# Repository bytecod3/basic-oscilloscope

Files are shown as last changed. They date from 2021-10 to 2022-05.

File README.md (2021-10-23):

# basic-oscilloscope
Basic Digital Storage Oscilloscope

## Introduction
This oscilloscope uses an STM32F103C8T6 blue pill board as the main MPU for processing and display of output

## Specifications
| Spec | Value |
| ----- | -------|
|Analog bandwidth| 0 - 500kHz|
|Number of channels| 2|
|Sample Rate| 2M Samples/s (configurable)|
|RAM| 2GB (External)|
|Processor| STM32F103C8T6|
|CPU-speed| 72MHz|
|Power input| 9V battery of 12V DC jack input|
|Current| 150mA|
|Screen size| 1.8”|
|Maximum input voltage| 50V pk-pk|
|Time base range| 10uS/Div - 500s/Div|
|Storage| USB-2.0 External flash drive|
|Coupling| AC, DC, GND|
|Input impedance| 1MOhm|
|Record length| 1024|

### Top View
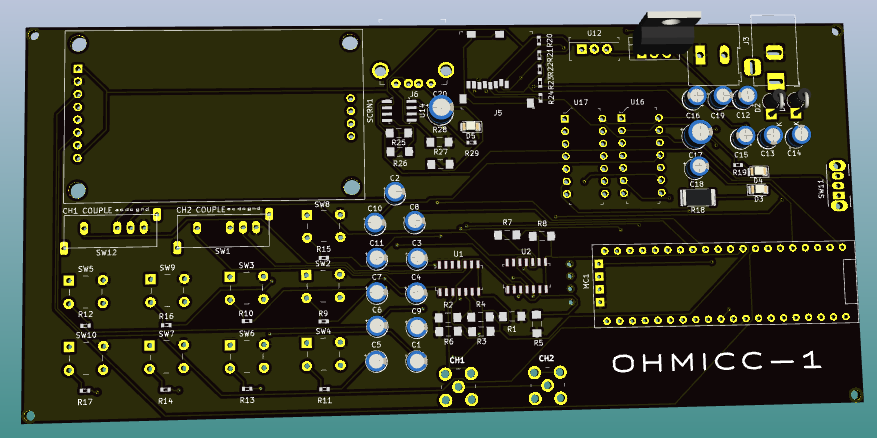
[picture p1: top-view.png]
Top View


### Bottom View
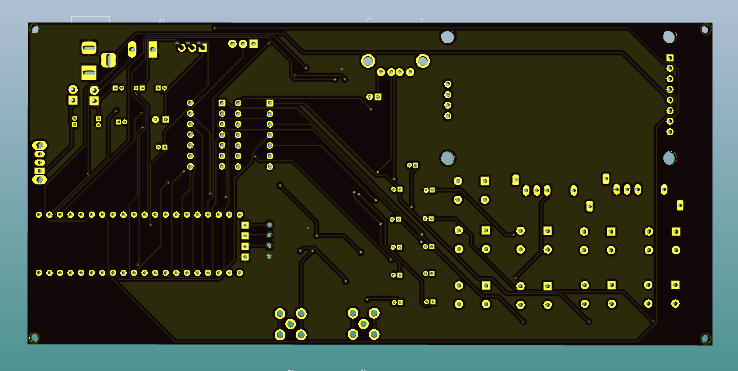
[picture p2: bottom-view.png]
Bottom View


### Left View
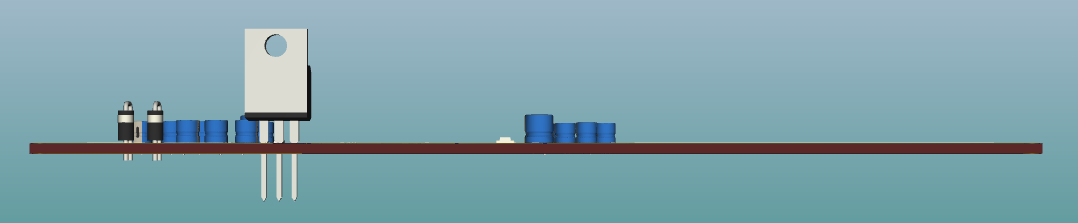
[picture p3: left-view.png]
Left View


### Right View
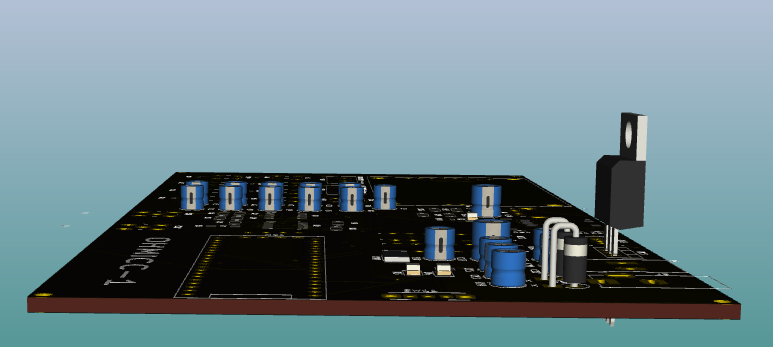
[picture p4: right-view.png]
Right View


## Usage
### Powering 
The oscilloscope uses either 12V DC jack adapter or a 9V battery. You can only use one at a time. 
To use the 12V adapter, plug in the jack into the DC Jack located at the top right of the board. To use the 9V battery,
you should have a battery holder with two wires protruding, for +ve and -ve side. Fix these wires on the terminal block located at the top right corner of the board. 
Finally is to toggle the slide-switch located on the right edge of the board.  
On both cases, a green LED should light indicating that the oscilloscope is fully powered. 

To switch off the oscilloscope, toggle the slide-switch agin to the direction labelled OFF on the board silkscreen.

**CAUTION**: Do not use both 12V adapter and 9V at the same time

## Callibration

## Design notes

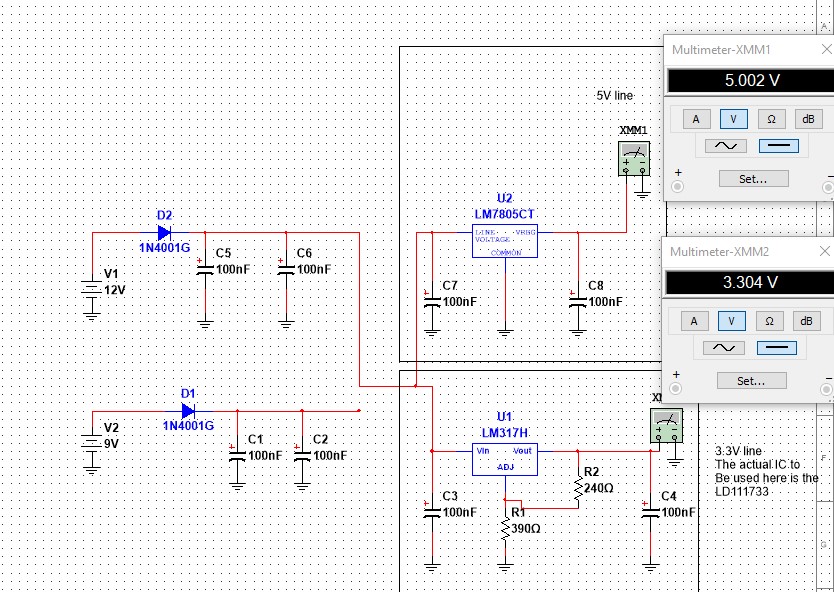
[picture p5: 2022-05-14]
simulations/power-supply/power-supply-simulation.jpg

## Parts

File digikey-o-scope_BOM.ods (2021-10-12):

Reference | Quantity | Value | Footprint | Digi-Key_PN | MPN | Price | Total Price | Part Page
C12 C13 C14 C15 C16 C18 | 6 | 100n | Capacitor_THT:CP_Radial_D4.0mm_P1.50mm | 493-12784-1-ND | UVR1H0R1MDD6TP | $0.30 | $1.80 | https://www.digikey.com/en/products/detail/nichicon/UVR1H0R1MDD6TP/4328371?s=N4IgTCBcDaICwE4DMBaAjGA7ADjulAcgCIgC6AvkA
C17 | 1 | 0.22u | Capacitor_THT:CP_Radial_D5.0mm_P2.50mm | 493-11478-1-ND | URS1HR22MDD1TD | $0.37 | $0.37 | https://www.digikey.com/en/products/detail/nichicon/URS1HR22MDD1TD/4320225?s=N4IgTCBcDaIKoCUDKBGAEgsYCyARXKAKriALoC%2BQA
C20 | 1 | 22u | Capacitor_THT:CP_Radial_D5.0mm_P2.00mm | 1572-1384-ND | 226CKR050M | $0.19 | $0.19 | https://www.digikey.com/en/products/detail/illinois-capacitor/226CKR050M/5411619?s=N4IgTCBcDa5gbAYQNICUAMBWdBZEBdAXyA
C1 C2 C3 C4 C5 C6 C7 C8 C9 C10 C11 C19 | 12 | 0.1u | Capacitor_THT:CP_Radial_D4.0mm_P1.50mm | 493-12784-1-ND | UVR1H0R1MDD6TP | $0.30 | $3.60 | https://www.digikey.com/en/products/detail/nichicon/UVR1H0R1MDD6TP/4328371?s=N4IgTCBcDaICwE4DMBaAjGA7ADjulAcgCIgC6AvkA
D1 D2 | 2 | D | Diode_THT:D_DO-41_SOD81_P2.54mm_Vertical_KathodeUp | 1N4148-P-GICT-ND | 1N4148-P-TR | $0.17 | $0.34 | https://www.digikey.com/en/products/detail/vishay-general-semiconductor-diodes-division/1N4148-P-TR/4826413
D3 D4 D5 | 3 | LED | LED_SMD:LED_1206_3216Metric | 2460-L152L-LWCTR-ND | L152L-LWC | $0.37 | $1.11 | https://www.digikey.com/en/products/detail/american-opto-plus-led/L152L-LWC/12325421
J1 J2 | 2 | 5-1814400-1 | digikey-footprints:RF_SMA_RightAngle_5-1814400-1 | 2057-RF1-07-T-00-75-ND | RF1-07-T-00-75 | $2.49 | $4.98 | https://www.digikey.com/en/products/detail/adam-tech/RF1-07-T-00-75/9832650
J3 | 1 | Jack-DC | Connector_BarrelJack:BarrelJack_Horizontal | 2073-DCJ200-10-A-K1-K-ND | DCJ200-10-A-K1-K | $0.74 | $0.74 | https://www.digikey.com/en/products/detail/gct/DCJ200-10-A-K1-K/9859579
J4 | 1 | Screw_Terminal_01x02 | TerminalBlock:TerminalBlock_Altech_AK300-2_P5.00mm | 1801135-ND | 1801135 | $1.09 | $1.09 | https://www.digikey.com/en/products/detail/phoenix-contact/1801135/4387899?s=N4IgTCBcDaIIwA4AMc4GYCsBaAcgERAF0BfIA
J5 | 1 | Micro_SD_Card | digikey-footprints:MicroSD_2908-05WB-MG | 3M5607CT-ND | 2908-05WB-MG | $3.48 | $3.48 | https://www.digikey.com/en/products/detail/3m/2908-05WB-MG/1242497?s=N4IgTCBcDa4JwAYAcBaBBWA6gIRQWQHEQBdAXyA
J6 | 1 | USB_A | digikey-footprints:USB_A_Female_UE27AC54100 | UE27AC54100-ND | UE27AC54100 | $0.70 | $0.70 | https://www.digikey.com/en/products/detail/amphenol-icc-commercial-products/UE27AC54100/1972253?s=N4IgTCBcDaIKoFEwHYCCBhArAFgIwAZ8QBdAXyA
MC1 | 1 | BLUE-PILL | my-screen:BLUE-PILL | * | * |  | $0.00 | *
R9 R10 R11 R12 R13 R14 R15 R16 R17 R29 | 10 | 1k | digikey-footprints:0603 | 13-RE0603FRE071KLTR-ND | RE0603FRE071KL | $0.10 | $1.00 | https://www.digikey.com/en/products/detail/yageo/RE0603FRE071KL/5923313
R18 | 1 | 100R | Resistor_SMD:R_2512_6332Metric | RMCF2512JT100RTR-ND | RMCF2512JT100R | $0.30 | $0.30 | https://www.digikey.com/en/products/detail/stackpole-electronics-inc/RMCF2512JT100R/1756924?s=N4IgTCBcDaIEoFkDCAxMBWAjGAUgFUwAZC4QBdAXyA
R19 | 1 | 160R | digikey-footprints:0603 | 749-1765-2-ND | MCT06030C1600FP500 | $0.13 | $0.13 | https://www.digikey.com/en/products/detail/vishay-beyschlag-draloric-bc-components/MCT06030C1600FP500/7347856?s=N4IgTCBcDaIOwBYCcBaAjHAbAVhWFAcgCIgC6AvkA
R20 R21 R22 R23 R24 | 5 | 22k | digikey-footprints:0603 | RNCF0603DTE22K0TR-ND | RNCF0603DTE22K0 | $0.13 | $0.65 | https://www.digikey.com/en/products/detail/stackpole-electronics-inc/RNCF0603DTE22K0/6264113
R1 R2 R3 R4 R5 R6 R7 R8 R25 R26 R27 R28 | 12 | 10k | digikey-footprints:1206 | 13-RE1206FRE0710KLTR-ND | RE1206FRE0710KL | $0.10 | $1.20 | https://www.digikey.com/en/products/detail/yageo/RE1206FRE0710KL/5924263?s=N4IgTCBcDaIEoFECMYAMA2AYo1B2JqA0gDIgC6AvkA
SCRN1 | 1 | 1.8"LCD_TFT | my-screen:1.8TFT_SCREEN | * | * |  | $0.00 | *
SW11 | 1 | SW_SPDT | Button_Switch_THT: SW_CuK_OS102011MA1QN1_SPDT_Angled | 2368-54-720-ND | 54-720 | $1.31 | $1.31 | https://www.digikey.com/en/products/detail/nte-electronics-inc/54-720/11647518
SW1 SW12 | 2 | SW_SP3T | my-screen:SP3T_OS103012MU1QP1_SWITCH | CKN9552-ND | OS103012MU1QP1 | $0.85 | $1.70 | https://www.digikey.com/en/products/detail/c-k/OS103012MU1QP1/1981423?s=N4IgTCBcDaIPIGUCMAGAzCpYCyBVJAigApIgC6AvkA
SW2 SW3 SW4 SW5 SW6 SW7 SW8 SW9 SW10 | 9 | SW_MEC_5E | digikey-footprints:Switch_Tactile_THT_6x6mm_MJTP1230 | 679-2428-ND | MJTP1230 | $0.10 | $0.90 | https://www.digikey.com/en/products/detail/apem-inc/MJTP1230/1798037
U12 | 1 | LD1117V33 | digikey-footprints:TO-220-3 | 497-1491-5-ND | LD1117V33 | $0.70 | $0.70 | https://www.digikey.com/en/products/detail/stmicroelectronics/LD1117V33/586012
U13 | 1 | LM7805_TO220 | Package_TO_SOT_THT:TO-220-3_Vertical | 2156-LM7805CT-ND | LM7805CT | $1.11 | $1.11 | https://www.digikey.com/en/products/detail/fairchild-semiconductor/LM7805CT/12600247
U14 | 1 | LM3526-L | digikey-footprints:SOIC-8_W3.9mm | LM3526MX-L/NOPBCT-ND | LM3526MX-L/NOPB | $1.26 | $1.26 | https://www.digikey.com/en/products/detail/texas-instruments/LM3526MX-L-NOPB/367056
U16 U17 | 2 | SN74HC14N | digikey-footprints:DIP-14_W3mm | 296-1577-5-ND | SN74HC14N | $0.23 | $0.46 | https://www.digikey.com/en/products/detail/texas-instruments/SN74HC14N/13504773
U1 U2 | 2 | LM324ADR | digikey-footprints:SOIC-14_W3.9mm | 296-9540-1-ND | LM324ADR | $0.49 | $0.98 | https://www.digikey.com/en/products/detail/texas-instruments/LM324ADR/381227?s=N4IgTCBcDa4JwDYC0cCsAWADEgjEgcgCIgC6AvkA

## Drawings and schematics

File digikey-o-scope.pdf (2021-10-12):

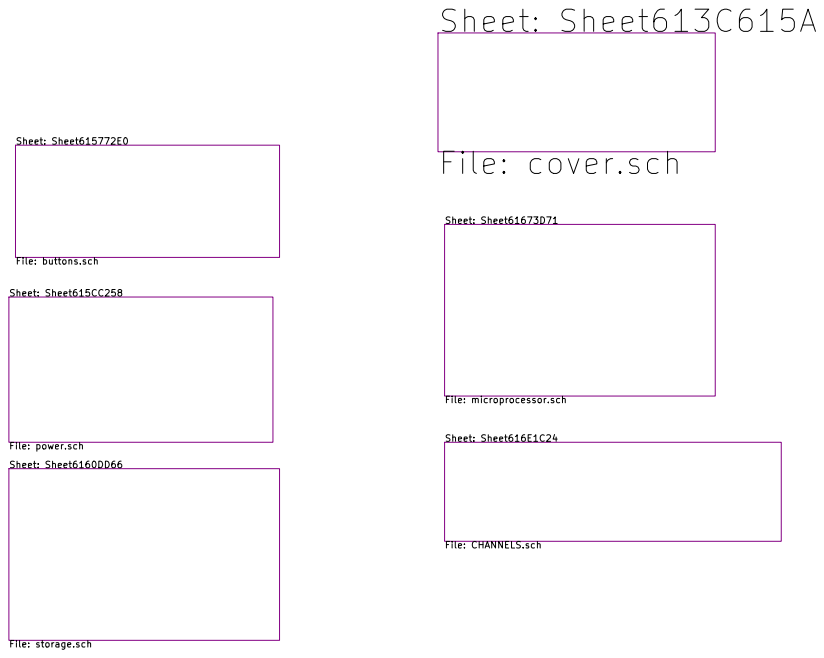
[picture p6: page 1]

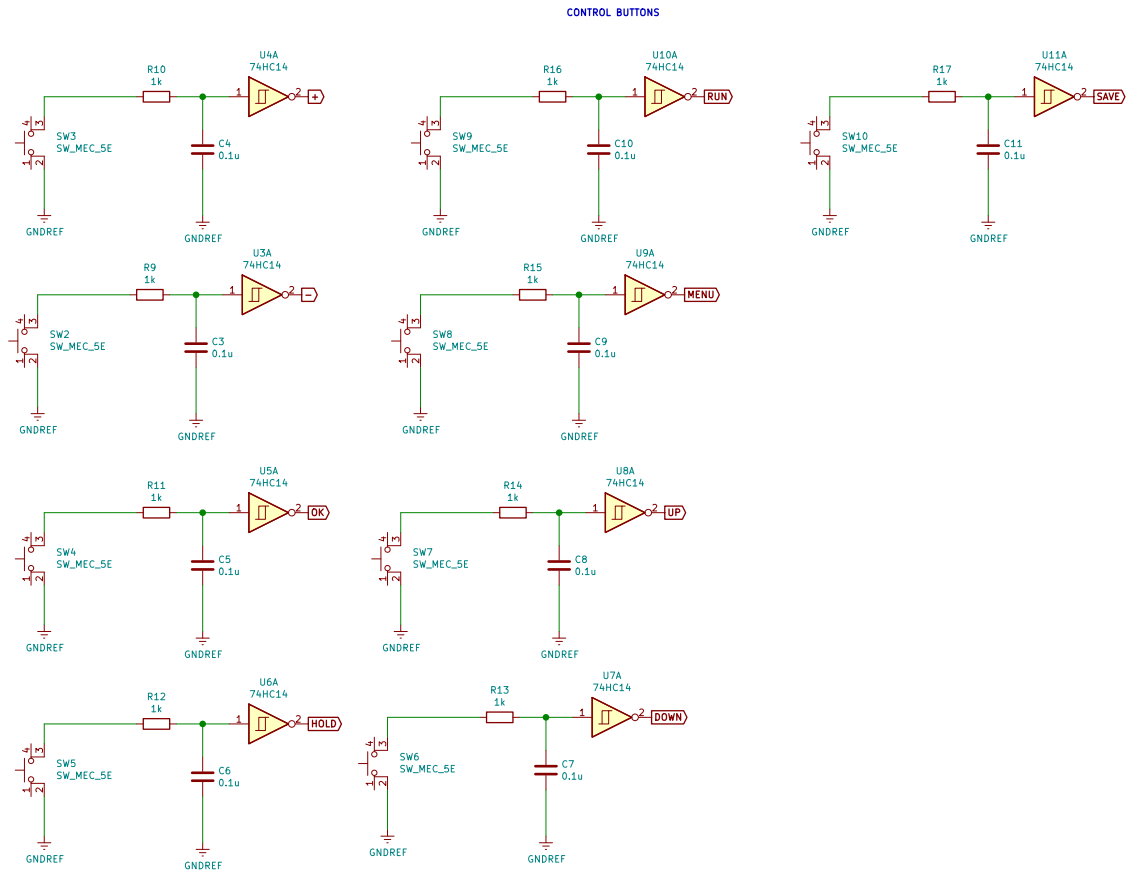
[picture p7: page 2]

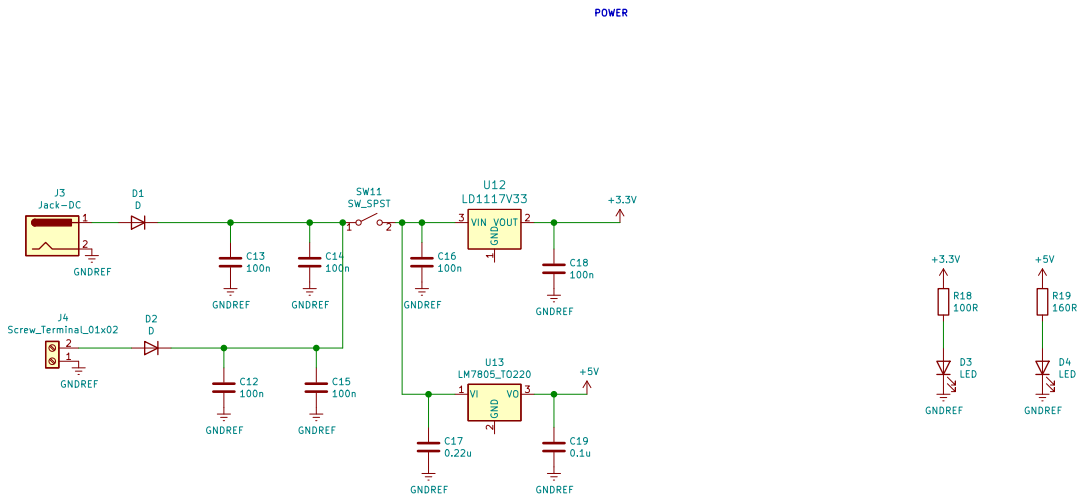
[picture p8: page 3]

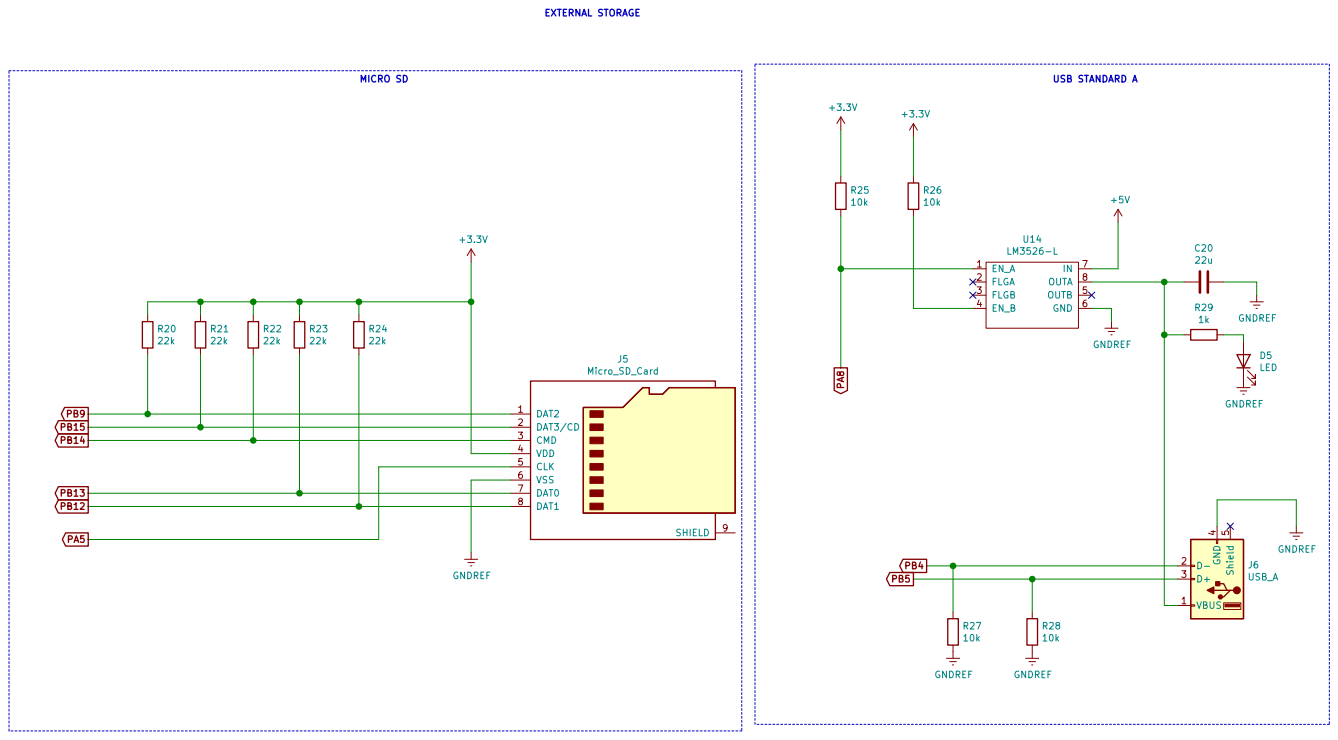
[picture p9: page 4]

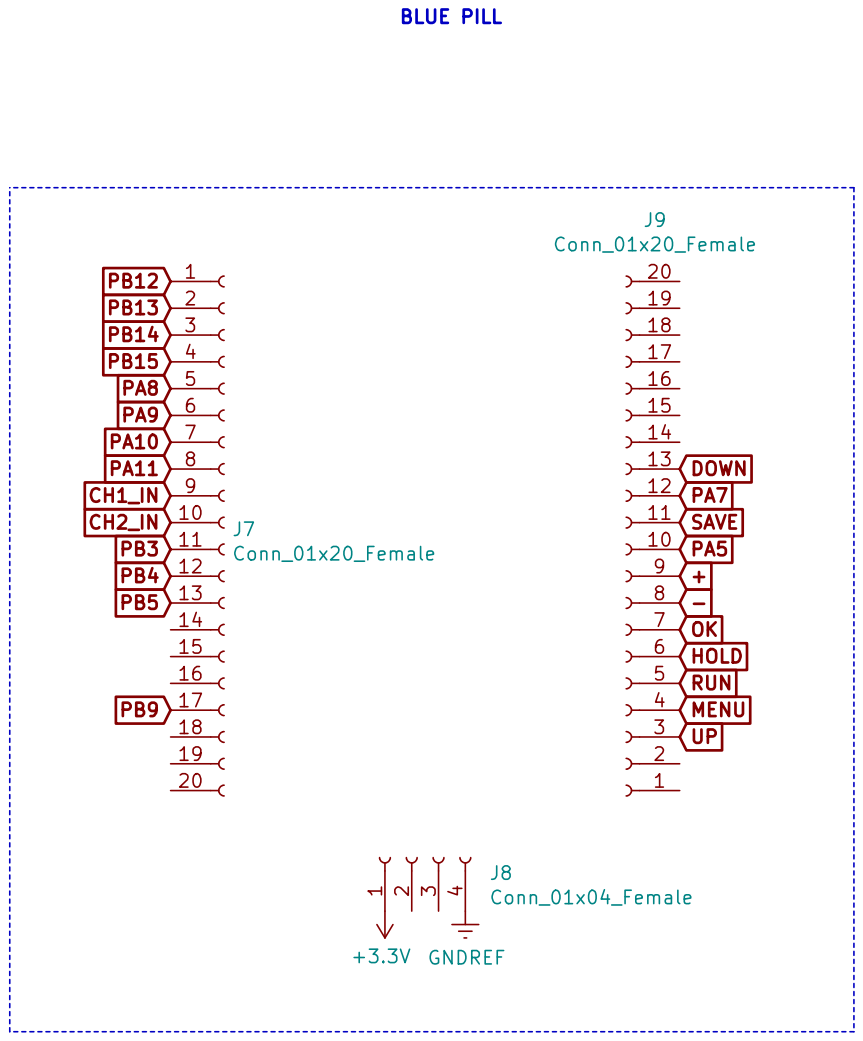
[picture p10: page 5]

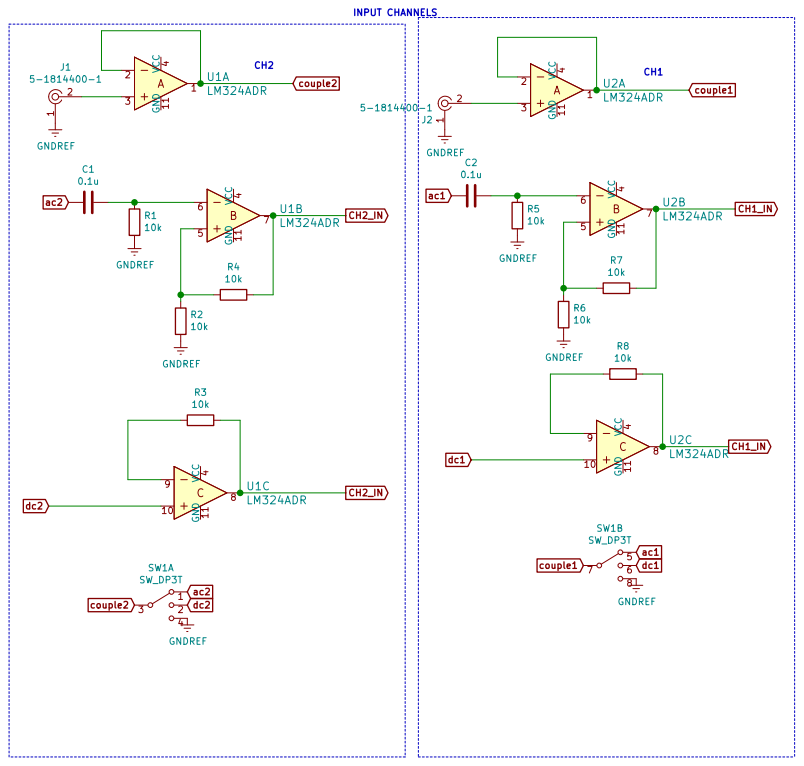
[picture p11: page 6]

ARM-CORTEX-M3 MINI OSCILLOSCOPE

Designed By: Edwin Mwiti, Ohmicc Hardware

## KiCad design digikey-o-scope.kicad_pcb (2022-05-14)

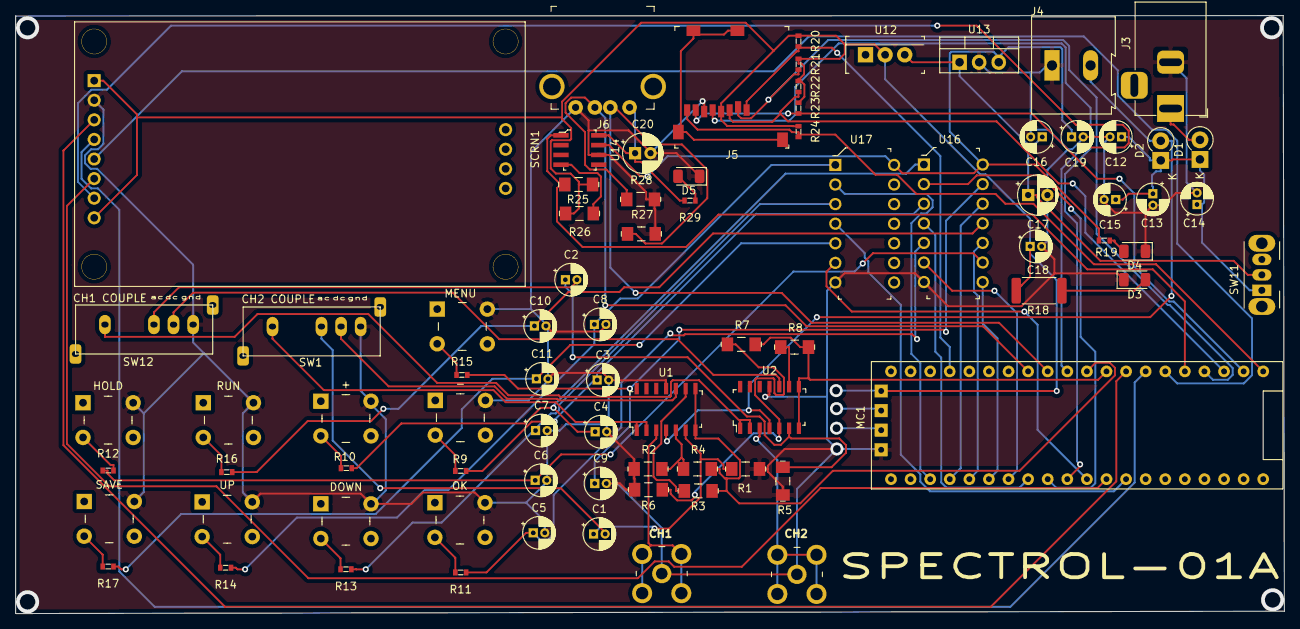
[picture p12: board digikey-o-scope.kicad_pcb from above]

Board: 2 copper layers, 164.5 x 77.5 mm, 81 parts (0 on the bottom side), 69 nets.

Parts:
+: SW_MEC_5E; Switch_Tactile_THT_6x6mm_MJTP1230
-: SW_MEC_5E; Switch_Tactile_THT_6x6mm_MJTP1230
C1, C2, C3, C4, C5, C6, C7, C8, C9, C10, C11, C19: 0.1u; CP_Radial_D4.0mm_P1.50mm
C12, C13, C14, C15, C16, C18: 100n; CP_Radial_D4.0mm_P1.50mm
C17: 0.22u; CP_Radial_D5.0mm_P2.50mm
C20: 22u; CP_Radial_D5.0mm_P2.00mm
D1, D2: D; D_DO-41_SOD81_P2.54mm_Vertical_KathodeUp
D3, D4, D5: LED; LED_1206_3216Metric
DOWN: SW_MEC_5E; Switch_Tactile_THT_6x6mm_MJTP1230
HOLD: SW_MEC_5E; Switch_Tactile_THT_6x6mm_MJTP1230
J1, J2: 5-1814400-1; RF_SMA_RightAngle_5-1814400-1
J3: 12V IN; BarrelJack_Horizontal
J4: Screw_Terminal_01x02; TerminalBlock_Altech_AK300-2_P5.00mm
J5: Micro_SD_Card; MicroSD_2908-05WB-MG
J6: USB_A; USB_A_Female_UE27AC54100
MC1: BLUE-PILL
MENU: SW_MEC_5E; Switch_Tactile_THT_6x6mm_MJTP1230
OK: SW_MEC_5E; Switch_Tactile_THT_6x6mm_MJTP1230
R1, R2, R3, R4, R5, R6, R7, R8, R25, R26, R27, R28: 10k; 1206
R9, R10, R11, R12, R13, R14, R15, R16, R17, R29: 1k; 0603
R18: 100R; R_2512_6332Metric
R19: 160R; 0603
R20, R21, R22, R23, R24: 22k; 0603
RUN: SW_MEC_5E; Switch_Tactile_THT_6x6mm_MJTP1230
SAVE: SW_MEC_5E; Switch_Tactile_THT_6x6mm_MJTP1230
SCRN1: 1.8"LCD_TFT; 1.8TFT_SCREEN
SW1, SW12: SW_SP3T; SP3T_OS103012MU1QP1_SWITCH
SW11: SPDT; SW_CuK_OS102011MA1QN1_SPDT_Angled
U1, U2: LM324ADR; SOIC-14_W3.9mm
U12: LD1117V33; TO-220-3
U13: LM7805_TO220; TO-220-3_Vertical
U14: LM3526-L; SOIC-8_W3.9mm
U16, U17: SN74HC14N; DIP-14_W3mm
UP: SW_MEC_5E; Switch_Tactile_THT_6x6mm_MJTP1230

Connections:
+: MC1.29, U16.2
+3V3: C18.1, J5.4, MC1.41, R18.1, R20.1, R21.1, R22.1, R23.1, R24.1, R25.1, R26.1, SCRN1.5, SCRN1.12, U12.2
+5V: C19.1, R19.1, U13.3, U14.7, U16.14, U17.14
+9V: D2.2, J4.2, U1.4, U2.4
-: MC1.28, U16.4
CH1_IN: MC1.9, R7.2, R8.2, U2.7, U2.8
CH2_IN: MC1.10, R3.2, R4.2, U1.7, U1.8
DOWN: MC1.33, U17.4
GNDREF: +.2, -.2, C3.2, C4.2, C5.2, C6.2, C7.2, C8.2, C9.2, C10.2, C11.2, C12.2, C13.2, C14.2, C15.2, C16.2, C17.2, C18.2, C19.2, C20.2, D3.1, D4.1, D5.1, DOWN.2, HOLD.2, J1.1, J2.1, J3.2, J4.1, J5.6, J6.4, MC1.44, MENU.2, OK.2, R1.1, R2.1, R5.1, R6.1, R27.2, R28.2, RUN.2, SAVE.2, SCRN1.6, SW1.4, SW12.4, U1.11, U2.11, U13.2, U14.6, U16.7, U17.7, UP.2
HOLD: MC1.26, U16.8
MENU: MC1.24, U16.12
unnamed: C1.1, R1.2, U1.6
unnamed: C2.1, R5.2, U2.6
unnamed: C3.1, R9.1, U16.3
unnamed: C4.1, R10.1, U16.1
unnamed: C5.1, R11.1, U16.5
unnamed: C6.1, R12.1, U16.9
unnamed: C7.1, R13.1, U17.3
unnamed: C8.1, R14.1, U17.1
unnamed: C9.1, R15.1, U16.13
unnamed: C10.1, R16.1, U16.11
unnamed: C11.1, R17.1, U17.5
unnamed: C12.1, C13.1, C14.1, C15.1, D1.1, D2.1, SW11.1
unnamed: C16.1, C17.1, SW11.2, U12.3, U13.1
unnamed: C20.1, J6.1, R29.2, U14.8
unnamed: D1.2, J3.1
unnamed: D3.2, R18.2
unnamed: D4.2, R19.2
unnamed: D5.2, R29.1
unnamed: J1.2, U1.3
unnamed: J2.2, U2.3
unnamed: R2.2, R4.1, U1.5
unnamed: R3.1, U1.9
unnamed: R6.2, R7.1, U2.5
unnamed: R8.1, U2.9
unnamed: -.3, R9.2
unnamed: +.3, R10.2
unnamed: OK.3, R11.2
unnamed: HOLD.3, R12.2
unnamed: DOWN.3, R13.2
unnamed: R14.2, UP.3
unnamed: MENU.3, R15.2
unnamed: R16.2, RUN.3
unnamed: R17.2, SAVE.3
unnamed: R26.2, U14.4
OK: MC1.27, U16.6
PA5: J5.5, MC1.30
PA7: MC1.32, SCRN1.10
PA8: MC1.5, R25.2, U14.1
PA9: MC1.6, SCRN1.9
PA10: MC1.7, SCRN1.8
PA11: MC1.8, SCRN1.7
PB3: MC1.11, SCRN1.11
PB4: J6.2, MC1.12, R27.1
PB5: J6.3, MC1.13, R28.1
PB9: J5.1, MC1.17, R20.2
PB12: J5.8, MC1.1, R24.2
PB13: J5.7, MC1.2, R23.2
PB14: J5.3, MC1.3, R22.2
PB15: J5.2, MC1.4, R21.2
RUN: MC1.25, U16.10
SAVE: MC1.31, U17.6
UP: MC1.23, U17.2
ac1: C2.2, SW12.1
ac2: C1.2, SW1.1
couple1: SW12.3, U2.1, U2.2
couple2: SW1.3, U1.1, U1.2
dc1: SW12.2, U2.10
dc2: SW1.2, U1.10

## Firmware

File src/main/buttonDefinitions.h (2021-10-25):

#ifndef BUTTONDEFINITIONS _H
#define BUTTONDEFINITIONS _H

/* button pin definitions */
#define MENU  PC13
#define OK    PA2
#define PLUS  PA4
#define MINUS PA3
#define UP    PC14 
#define DOWN  PB0
#define SAVE  PA6
#define HOLD  PA1
#define RUN   PA0

/* Initial status settings */
unsigned int initial_button_status = 0x0;

/* debounce handling */
long TIME = 0;
long DEBOUNCE_DELAY = 200; // to check this callbration

#endif

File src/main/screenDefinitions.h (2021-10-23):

/* Definitions for screen pins going into the STM32 Board */

#define SCK 	PB3
#define SDA 	PA7
#define DC		PA9 // A0
#define RESET 	PA10
#define CS		PA11

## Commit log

2021-07-16 power supply branching
    [basic-oscilloscope.kicad_pcb, basic-oscilloscope.sch]
2021-07-17 implement reset and debounce
    [basic-oscilloscope.sch]
2021-07-18 add hardware debounce
    [basic-oscilloscope.sch]
2021-07-22 add voltage buffer for BNC channels
    [basic-oscilloscope.kicad_pcb, basic-oscilloscope.sch]
2021-07-22 add 5V label for buffer
    [basic-oscilloscope.sch, connectors.sch]
2021-08-12 create pcb layout
    [basic-oscilloscope.kicad_pcb, basic-oscilloscope.sch]
2021-09-02 update component footprints
    [basic-oscilloscope.kicad_pcb, basic-oscilloscope.sch, connectors.sch, coupling_switches.sch]
2021-10-12 add hierachical schematics
    [CHANNELS.sch, basic-oscilloscope.kicad_pcb, basic-oscilloscope.sch, buttons.sch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]
2021-10-23 create TFT screen definition and instance
    [screen.sch]
2022-05-14 added power supply simulations
    [CHANNELS.kicad_sch, buttons.kicad_sch, cover.kicad_sch, digikey-o-scope.kicad_pcb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]
